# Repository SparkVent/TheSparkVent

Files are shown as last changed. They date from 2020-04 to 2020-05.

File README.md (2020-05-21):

# The Campbell Spark Vent

The Campbell Spark Vent is an open-source Venturi-based ventilator design for emergency use during the COVID-19 pandemic.

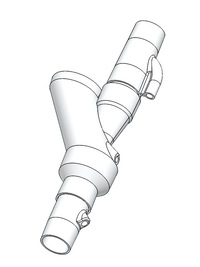
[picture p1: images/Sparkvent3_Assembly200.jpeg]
Sparkvent3 Assembly

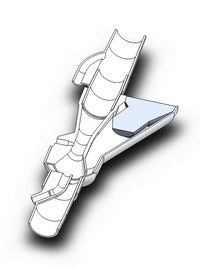
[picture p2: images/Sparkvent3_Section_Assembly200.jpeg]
Sparkvent3 Section_Assembly

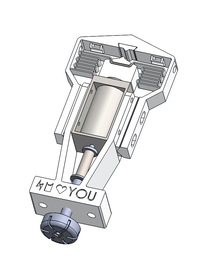
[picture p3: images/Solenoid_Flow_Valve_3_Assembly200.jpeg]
Solenoid Flow Valve 3 Assembly

Campbell SparkVent3 Venturi

Our aim is to make the simplest, safest ventilator we can for the lowest cost and the easiest to manufacture.

[Dr Duncan Campbell](http://www.anzca.edu.au/about-anzca/history-and-heritage/anaesthesia-stories/dr-duncan-campbell), the inventor of the [Campbell Ventilator](https://journals.sagepub.com/doi/pdf/10.1177/0310057X1204000601), created the initial Venturi circuit design as a means to provide a simple and safe ventilator design for the COVID-19 pandemic. The Venturi eliminates the need for bellows and hence, radically simplifies the design, construction and operation of the ventilator.

Our team has refined his original design to it's current version.

We provide this design to anyone who wishes to use it, make it or improve it to help save lives during the COVID-19 pandemic.

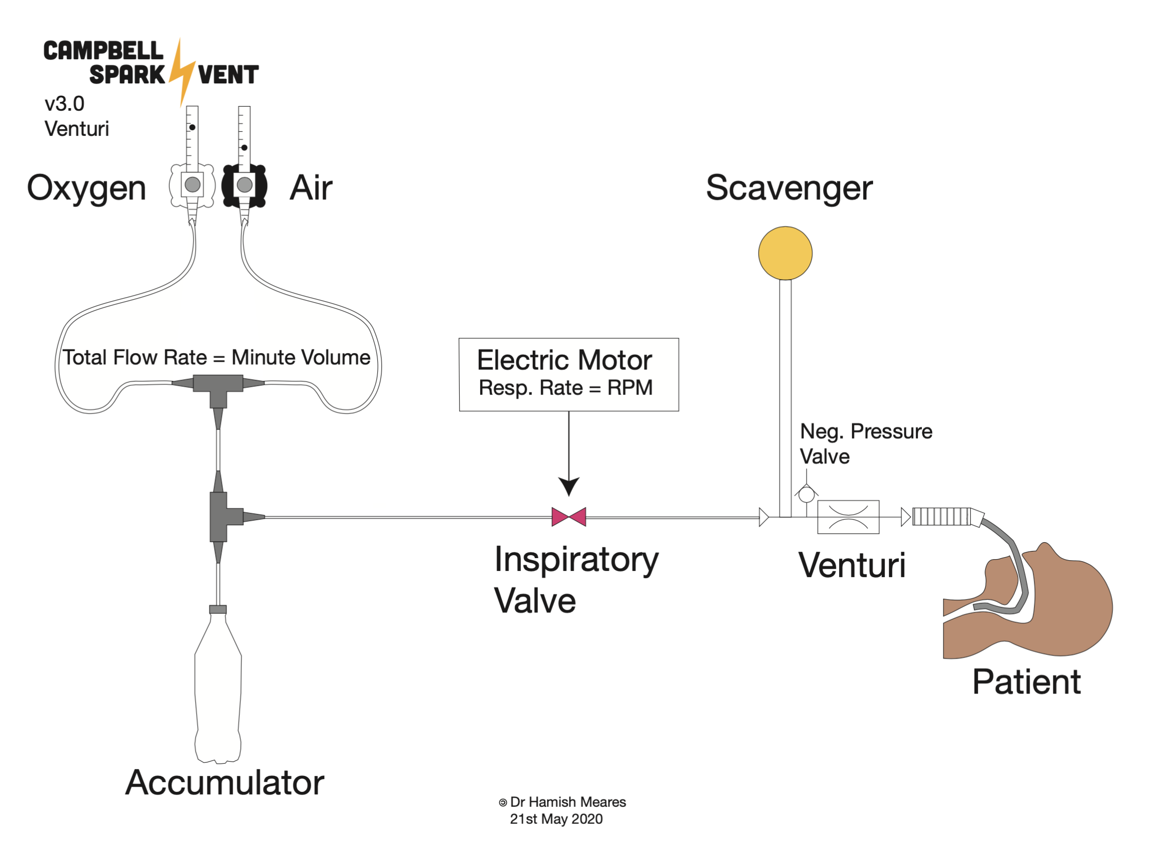
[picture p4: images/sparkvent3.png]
Overview

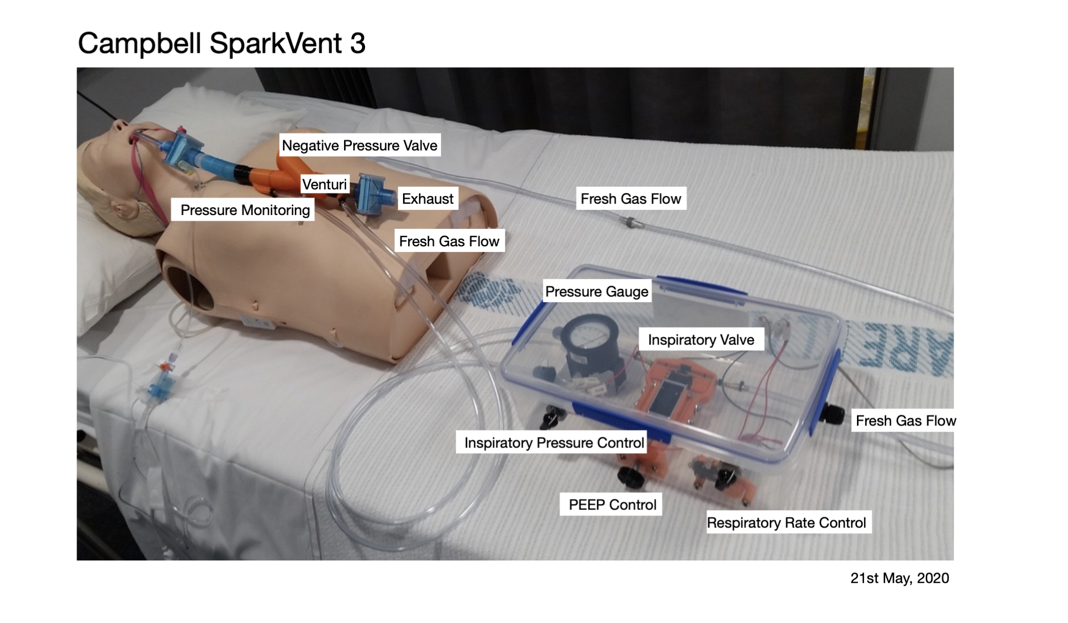
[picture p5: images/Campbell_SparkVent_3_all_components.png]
Campbell SparkVent3 all components

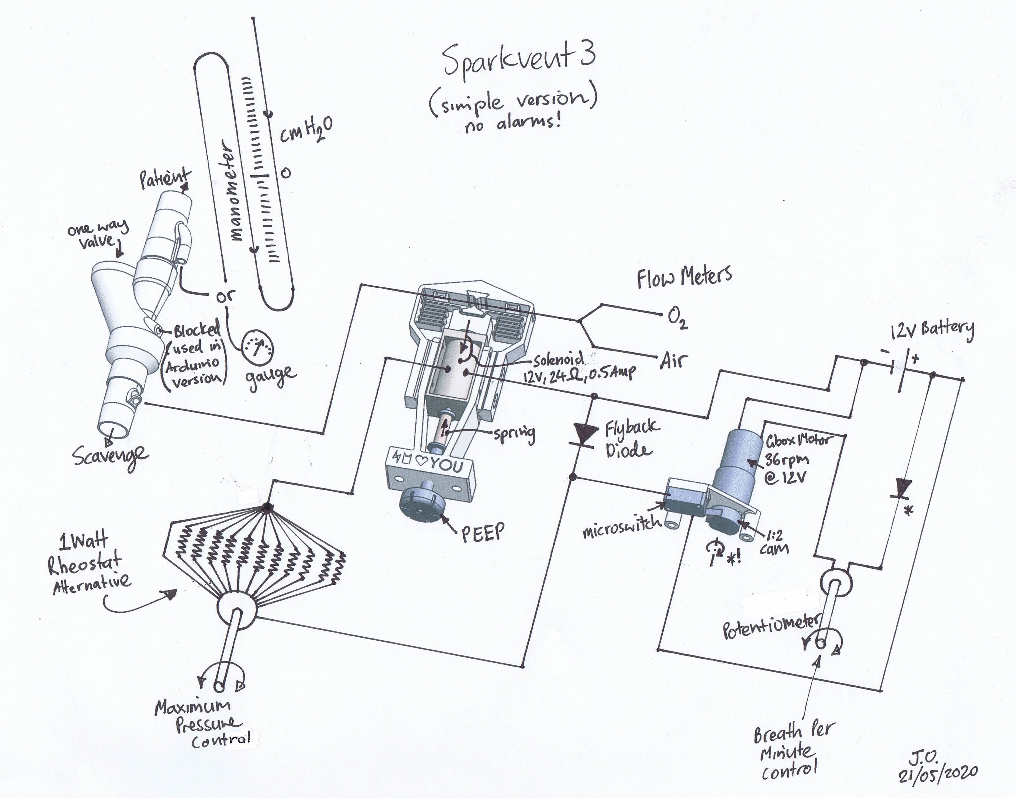
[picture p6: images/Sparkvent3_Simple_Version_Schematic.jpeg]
Sparkvent3 Simple Version Schematic


## Technical Details

The operator sets respiratory rate and also the minute volume and oxygen concentration using two flow meters for oxygen and air. The energy to drive the ventilator comes from the potential energy stored in the pressured gas. The only moving part in the ventilator is the inspiratory valve that operates via a solenoid that compresses a silicon tube that carries the fresh gas flow. The energy consumption of the solenoid valve is very low at around 6W and could be run from a battery if needed. The inspiratory and PEEP pressures are delivered via the venturi. Inspiratory pressure can be set by increasing the fresh gas flow rate, PEEP is set mechanically by turning a screw that sets the minimum pressure in the system. Pressure is monitored using a simple water manometer. The venturi mechanism provides a physical fail-safe as if the pressure in the fresh gas flow is increased to 400kPa (typical hospital gas pressure), the pressure delivered by the venturi is only around 5kPa, (50cmH2O) and the rest of the pressure is dissipated to the exhaust, as the narrow throat of the venturi naturally limits the pressure delivered.

The venturi must sit very close to the endotracheal tube to minimise dead space. The minimal dead space is necessary to minimise the time it takes for the system to reach it's target inspiratory pressure as ideally we would like a square wave pressure waveform.

This design is deliberately 'bare bones'. Ideally it should be used in conjunction with an oxygen saturation probe and an end-tidal carbon dioxide monitor to ensure the patient is adequately ventilated. We are in the process of adding a pressure and flow sensors so we can add alarm systems to this design.

### Aims

* **Works** - as close to these [TGA (Australian Regulatory Body) Guidelines](https://www.tga.gov.au/sites/default/files/ventilator-covid-19-use-australia.pdf) or the more extensive [UK Rapidly Manufactured Ventilator System Specifications](https://assets.publishing.service.gov.uk/government/uploads/system/uploads/attachment_data/file/876167/RMVS001_v3.1.pdf) as we can get it
* **Simple** - as we can get it
* **Safe** - as we can get it
* **Reliable** - as we can get it = ideally do 250,000 cycles without failure
* **Easy to make** - as we can get it
* **Made from existing medical equipment and easily-sourced industrial equipment** - where possible

### Immediate Goal
Provide a ventilator of last-resort for hospitals that have been overwhelmed by the sheer number of COVID-19 patients that require life-saving ventilation.

### Long term Goal
Develop a ventilator that could be used in developing countries to help save lives.

### Testing
We have performed bench testing of the pressure, flow and volume characteristics  on a test-lung in a hospital biomedical workshop (Graphs below). We are currently performing reliability testing of the solenoid 3D-printed valve. Next phase we will be adding alarms and usability testing.
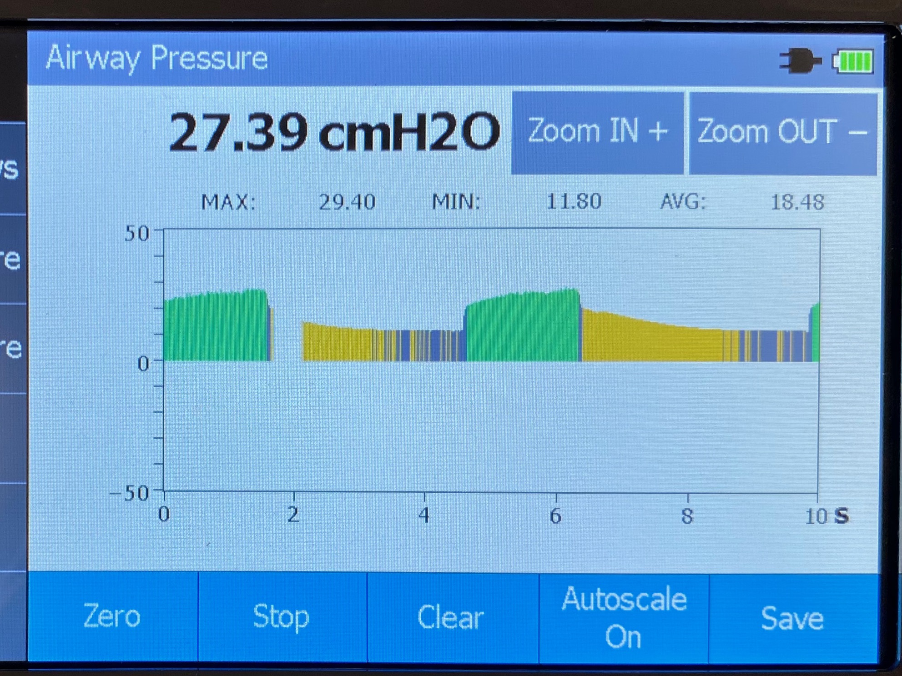
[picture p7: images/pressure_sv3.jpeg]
pressure graph

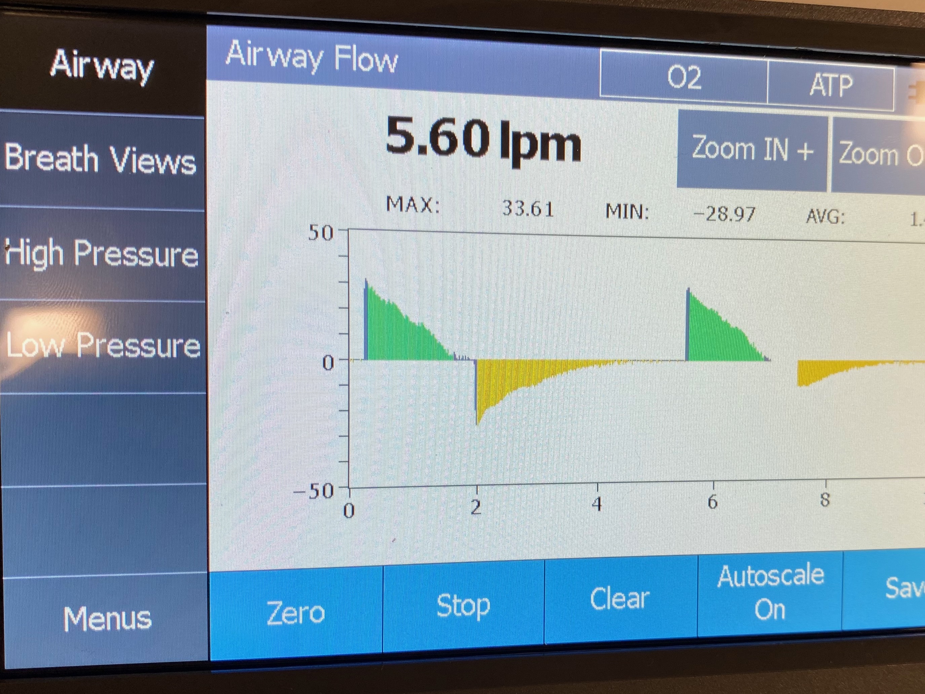
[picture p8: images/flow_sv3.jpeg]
flow graph

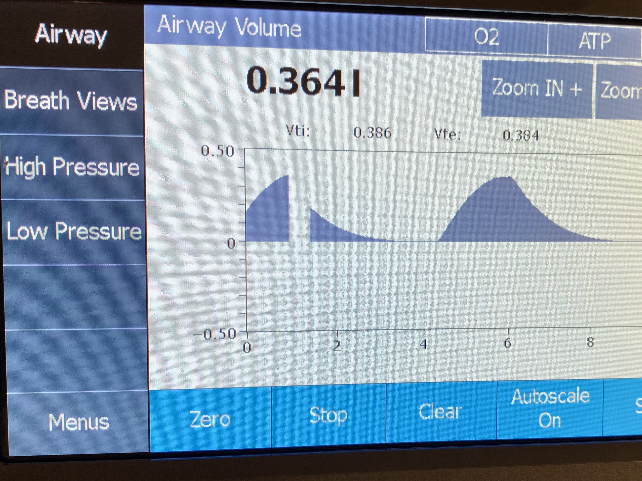
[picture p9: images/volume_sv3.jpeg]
volume graph


## Team

* Dr Hamish Meares, Anaesthetic Doctor/Engineer
* Dr Duncan Campbell, Anaesthetic Doctor (retired) /Inventor of the Campbell Ventilator
* Benjamin Brice, Industrial Designer
* Graham Brice, Biomedical Engineer
* Pete Micallef, CNC Tech & Design, Regal Machinery Services
* Jamie Oorschot, Mechanical Engineer
* Jeremy Funke, Electrical Engineer
* Ray Aunei Mose, Biomedical Engineer
* Peter Humble, IT / Web designer
* With some much appreciated mechanical design help from the University of Newcastle’s Discipline of Mechanical Engineering

## Much Appreciated Support

* [Hall & Wilcox Lawyers](https://hallandwilcox.com.au)
* Dr Carl Hughes, Anaesthetic Doctor & GP
* Dr David Campbell, Anaesthetic Doctor
* Dr Keith Streatfield, Anaesthetic Doctor
* Dr Steve Pickering, Anaesthetic Doctor

## Disclaimer
THE SPARK VENT HAS NOT BEEN TESTED FOR SAFETY AND ITS SAFETY AND PERFORMANCE HAS NOT BEEN EVALUATED OR CONFIRMED. IT SHOULD ONLY BE CONSIDERED FOR USE AS AN ABSOLUTE LAST-RESORT OPTION IN A LIFE-THREATENING EMERGENCY SITUATION. THIS VIDEO IS PROVIDED FOR EDUCATIONAL AND INFORMATIVE PURPOSES DURING A GLOBAL HEALTH EMERGENCY FOR THE CORONA VIRUS PANDEMIC. WE HAVE SOUGHT TO FOLLOW THE UK AND AUSTRALIAN GUIDELINES (TGA) FOR AN EMERGENCY VENTILATOR DESIGN FOR THE PANDEMIC BUT HAVE DEVIATED SIGNIFICANTLY WITH OUR CHOICE IN MATERIALS AND THE ABSENCE OF ANY ALARMS.

IN NO EVENT SHALL THE SPARKVENT TEAM, BE LIABLE TO ANY PARTY FOR DIRECT, INDIRECT, SPECIAL, INCIDENTAL, OR CONSEQUENTIAL DAMAGES, INCLUDING LOST PROFITS, ARISING OUT OF THE USE OF THESE SPECIFICATIONS, LIST OF MATERIALS, ELECTRONIC DESIGNS , SOFTWARE CODE AND ANY DOCUMENTATION, EVEN IF THE SPARKVENT TEAM HAS BEEN ADVISED OF THE POSSIBILITY OF SUCH DAMAGE. THE SPARKVENT TEAM DISCLAIMS ANY WARRANTIES, INCLUDING, BUT NOT LIMITED TO, THE IMPLIED WARRANTIES OF MERCHANTABILITY AND FITNESS FOR A PARTICULAR PURPOSE. THE SOFTWARE AND ACCOMPANYING DOCUMENTATION, SPECIFICATIONS, LIST OF MATERIALS, ELECTRONIC DESIGNS, SOFTWARE CODE AND ANY DOCUMENTATION IF PROVIDED HEREUNDER IS PROVIDED "AS IS". THE SPARKVENT HAS NO CLAIM THAT IT IS COMPLETED OR FUNCTIONAL AND HAS NO OBLIGATION TO PROVIDE MAINTENANCE, SUPPORT, UPDATES, ENHANCEMENTS, OR MODIFICATIONS. RISKS INCLUDE BUT ARE NOT LIMITED TO SERIOUS PHYSICAL INJURY, BURNS, DISABILITY AND/OR DEATH TO BOTH THE PATIENT AND THE OPERATOR.

## Copyright

<br /><span xmlns:dct="http://purl.org/dc/terms/" property="dct:title">SparkVent</span> by <a xmlns:cc="http://creativecommons.org/ns#" href="Sparkvent.org" property="cc:attributionName" rel="cc:attributionURL">SparkVent</a> is licensed under a <a rel="license" href="http://creativecommons.org/licenses/by-nc-sa/4.0/">Creative Commons Attribution-NonCommercial-ShareAlike 4.0 International License</a>.<br />Based on a work at <a xmlns:dct="http://purl.org/dc/terms/" href="Sparkvent.org" rel="dct:source">Sparkvent.org</a>.<br />Permissions beyond the scope of this license may be available at <a xmlns:cc="http://creativecommons.org/ns#" href="Sparkvent.org" rel="cc:morePermissions">Sparkvent.org</a>.

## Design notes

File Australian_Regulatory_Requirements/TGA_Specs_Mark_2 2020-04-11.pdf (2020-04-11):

Spark Vent Mark II

Mark II Mark II | Yes/No/Unknown/ InProgress/NA

## Required Features

### Mandatory ventilation

•the operator can set a tidal volume and respiratory rate. The output will be selected by the operator to be either pressure-controlled ventilation (PCV) or volume-controlled ventilation (VCV) | Yes

### Positive end expiratory pressure (PEEP)

•range from 5 to 25 cm H2O adjustable in increments of 2 cm H2O or smaller | Yes
•patient breathing system must remain pressurised to at least the PEEP level setting at all times | Yes

### Respiratory rate

•range from 5 to 30 breaths per minute adjustable in increments of 2 or smaller | Yes

### Tidal volume (Vt)

•range from at least 200 mL to 800 mL, adjustable in increments of 50 mL or smaller. | Yes
•inspiratory Jlow rate up to 100 litres per minute | Unknown
•inspiratory time adjustable from 0.5 seconds to 2 seconds | No

### Airway pressure safety

•peak inspiratory pressure should adapt to achieve the set tidal volume and… | No
•have an operator-adjustable limit up to 50 cm H2O | Yes
•a mechanical failsafe valve must open at 80 cm H2O | Yes

### Inspired oxygen proportion (FiO2)

•range up to 100%, adjustable in increments of 5% or smaller | Yes
•the ventilator must present 22 mm outside diameter (OD) ‘male’ standard connectors for connection to operator-supplied 22 mm ‘female’ connectors on the breathing system | Yes
•All elements in the gas pathway must meet biological safety and oxygen safety standards for 100% oxygen, especially to minimise risk of Jire or contamination of the patient’s airway | Unknown

### Oxygen supply to ventilator

•all gas connectors and hoses must use standard non-interchangeable connectors and be colour coded according to AS 2902-2005 or equivalent standards | Yes
•must connect to wall pipeline oxygen supply via Sleeve Index System (SIS) deJined in AS 2896-2011 or equivalent. Assume oxygen pipeline pressure is in the range 400 kPa (4 bar) to 500 kPa | Yes
•must be able to be operated on any attached oxygen cylinder connected via SIS and Jitted with a 400 kPa output regulator | Yes

### Air supply to ventilator

•it is preferable not to require pressurised air, as it will not be available in all care areas in pandemic conditions, however if pressurised air is required for ventilator operation: | Yes
•all gas connectors and hoses must use standard non-interchangeable connectors and be colour coded according to applicable standards | In Progress
•must connect to the wall pipeline air supply via SIS | Yes
•Assume wall pipeline pressure is in the range 400 kPa (4 bar) to 500 kPa | Yes

### Displays

•current settings of tidal volume, frequency, inspiratory time, PEEP, FiO2, ventilation mode:
•tidal volume | Yes
•frequency | Yes
•inspiratory time | No
•PEEP | Yes
•FiO2 | Yes
•ventilation mode | Yes
•mechanical displays on control devices such as knobs and sliders are acceptable | Yes

Mark II | Yes/No/Unknown/ InProgress/NA

### Alarms

Must generate an audible alarm at:
•gas or electricity supply failure | No
•machine switched off while connected to a patient | No
•inspiratory and PEEP pressure not achieved | No
•expiratory tidal volume not achieved by 10% | No
•inspiratory tidal volume exceeded by 10% | No

### Electricity supply

•240V AC mains | Yes
•20 minutes backup battery in case of mains electricity failure | No
•should avoid RF or EM emissions that could interfere with other critical machinery | Unknown

### Miscellaneous

•must achieve 100% operating duty cycle for at least 14 days | Unknown
•must include instructions for use and trouble shooting | In Progress
•clear labelling of all critical functions and controls using standard terms, pictograms and colours that will be readily recognised by Australian healthcare staff | In Progress
•must have transparent design, supply chain, manufacture and testing processes and Jield service arrangements that are of sufJicient quality to enable health department ofJicials and Therapeutic Goods Administration (TGA) ofJicials to deem them appropriate for usage in exceptional circumstances | No
•must be able to be moved easily within hospital premises | Yes
•must be amenable to standard disinfection and cleaning procedures | Yes
•must be made from materials and parts, including disposables, that are readily available in the Australian supply chain (anticipating increasing global restrictions on freight movement): | Yes
1. Materials of Construction (raw materials)
a.The chosen material must be reasonably pure and simple in nature (minimise the use of additives where possible) | Yes
a.For components requiring Jlexibility avoid the use of materials requiring plasticisers. Good candidates are those materials that belong to the polyoleJin family, examples include polyethylene and polypropylene | Yes
a.For structural components, materials such as polycarbonate or acrylonitrile butadiene styrene (ABS) should be used without additives, although reinforcement with glass Jibre would be acceptable | Yes
a.Polyvinyl chloride (PVC) must be avoided in the patient gas pathway | No
a.PVC should be avoided elsewhere | No

2.Manufacturing Process (risk from contaminants)
a.Mould release agents used within extrusion or injection moulding techniques may be required in setting up the machine, they should not be needed once a process is in full scale production | NA
a.Approximately, the Jirst 20 or so items in an injection moulding production run should be discarded to minimise risk from contamination with mould release agents | NA
a.Extrusion and moulding techniques are comparatively simple and well controlled; therefore, ventilators will not be required to be manufactured within cleanroom speciJications | NA
a.Manufacture in a reasonably clean room and protection of components and products from contamination should sufJice | Yes

a.If a-d above are followed, chemical or particulate testing of the air coming out of the breathing circuit should not be necessary

3. Hazard Mitigation
a.Particulate matter: solid particles suspended in a gas. Particulate matter emissions are not of signiJicant concern if the manufacturing process is adequately controlled as per the above criteria | Unknown
a.Volatile organic compound (VOC): organic compound whose boiling point is in the range of 50⁰C to 260⁰C. Risk of exposure to VOCs can be minimised through the appropriate choice of materials as set out in section 1 (materials of construction) | Yes
a.Leachable substances (in condensate): chemicals removed from the medical device by the action of water, other liquids or other gases related to the use of the medical device. Ensure an HME Jilter is used between the ventilator and breathing system. | Yes

### Other relevant standards

| Yes/No/Unknown/ InProgress/NA

•See Appendix A, Relevant Standards and Documents
•Device veriJication and validation testing must be carried out by the manufacturer. Testing should be aligned to the requirements in the UK MHRA guidelines in Appendix B (Testing protocol for Jinal validation of safety and performance of RVMS) at | In Progress

https://assets.publishing.service.gov.uk/government/uploads/system/uploads/attachment_data/Jile/876167/RMVS001_v3.1.pdf (https://assets.publishing.service.gov.uk/government/uploads/system/uploads/attachment_data/file/876167/RMVS001_v3.1.pdf)

•Rapidly manufactured ventilators are likely to include software. Included software falls under the deJinition of a medical device and must meet requirements that will ensure product performance and safety. See Appendix C (software development requirements) from the MHRA guideline at the link above. | No

## Desirable Features

### Spontaneous ventilation

•the operator sets an inspiratory pressure and PEEP. The ventilator will sense when a patient starts to breathe in and apply the operator-speciJied inspiratory pressure, then sense when the patient starts to breathe out and apply the operator-speciJied expiratory pressure. | No
•If the patient stops breathing in pressure support mode, it must failsafe automatically to mandatory ventilation. | Yes

### Synchronized mandatory ventilation

•same as mandatory ventilation but mandatory breaths are synchronized to patient effort through Jlow sensing or pressure sensing, also known as synchronized intermittent mandatory ventilation volume control (SIMV-VC) or pressure control (SIMV-PC) | No
•additional inspiratory pressure support for those patients breathing to some extent themselves. | No

### Tidal volume

•capacity to set inspiratory rise-time as a fraction of the inspiratory time, through waveform control or ratio control. | No
•inspiratory Jlow rate up to 150 litres per minute | Unknown

### Exhalation filters

•use modular expiratory components that can be removed for disinfection, and that can vent to long life viral Jilters | Yes

### Gas supply

•can operate using an oxygen concentrator device for input oxygen | Unknown

### Extended battery use

•hot swappable batteries to run on battery supply for an extended period, for example, 2 hours for within-hospital transfer | In Progress

### Alarms

•inspiratory airway pressure exceeded | No
•respiratory rate exceeds a set limit | No

### Displays

•actual achieved measurements of tidal volume, breathing rate, PEEP, peak and plateau pressure, FiO2, inspiratory to expiratory time ratio (I:E) | No
•displayed waveforms of key parameters including but not limited to Jlow, pressure and volume versus time | No
•if it exists, in pressure support mode there must be real-time conJirmation of each patient breath and an alarm if below acceptable range | No

Notes

PCV you set pressures not volumes, you can measure the volumes delivered though

Ventilator has a fixed I:E ratio of one to two, and hence Inspiratory time will be dependent on respiratory rate

Pressure control ventilation mode only, not pressure-volume-guaranteed. Needs operator to adjust pressure to achieve target volume

Pop off at 40cm H20

Does not use 4 bar gas supply directly, instead it uses Australian standard flow meters attached to the 4 bar supply

Uses Standard Sleeve Index as ventilator uses standard flow meters that already meet the Australian Standards.

Requires pressured gas supply, but is very frugal in it’s use, only the patient’s minute volume so around 5-10 L/ min

Uses Standard Sleeve Index as ventilator uses standard flow meters that already meet the Australian Standards.

Fixed I:E ratio 1:2, so inspiratory time will be dependent on respiratory rate

Only does PCV

## Required Features

### Mandatory ventilation

•the operator can set a tidal volume and respiratory rate. The output will be selected by the operator to be either pressure-controlled ventilation (PCV) or volume-controlled ventilation (VCV)

### Positive end expiratory pressure (PEEP)

•range from 5 to 25 cm H2O adjustable in increments of 2 cm H2O or smaller
•patient breathing system must remain pressurised to at least the PEEP level setting at all times

### Respiratory rate

•range from 5 to 30 breaths per minute adjustable in increments of 2 or smaller

### Tidal volume (Vt)

•range from at least 200 mL to 800 mL, adjustable in increments of 50 mL or smaller. •inspiratory Jlow rate up to 100 litres per minute
•inspiratory time adjustable from 0.5 seconds to 2 seconds

### Airway pressure safety

•peak inspiratory pressure should adapt to achieve the set tidal volume and…

•have an operator-adjustable limit up to 50 cm H2O
•a mechanical failsafe valve must open at 80 cm H2O

### Inspired oxygen proportion (FiO2)

•range up to 100%, adjustable in increments of 5% or smaller
•the ventilator must present 22 mm outside diameter (OD) ‘male’ standard connectors for connection to operator-supplied 22 mm ‘female’ connectors on the breathing system
•All elements in the gas pathway must meet biological safety and oxygen safety standards for 100% oxygen, especially to minimise risk of Jire or contamination of the patient’s airway

### Oxygen supply to ventilator

•all gas connectors and hoses must use standard non-interchangeable connectors and be colour coded according to AS 2902-2005 or equivalent standards
•must connect to wall pipeline oxygen supply via Sleeve Index System (SIS) deJined in AS 2896-2011 or equivalent. Assume oxygen pipeline pressure is in the range 400 kPa (4 bar) to 500 kPa
•must be able to be operated on any attached oxygen cylinder connected via SIS and Jitted with a 400 kPa output regulator

### Air supply to ventilator

•it is preferable not to require pressurised air, as it will not be available in all care areas in pandemic conditions, however if pressurised air is required for ventilator operation:
•all gas connectors and hoses must use standard non-interchangeable connectors and be colour coded according to applicable standards
•must connect to the wall pipeline air supply via SIS
•Assume wall pipeline pressure is in the range 400 kPa (4 bar) to 500 kPa

### Displays

•current settings of tidal volume, frequency, inspiratory time, PEEP, FiO2, ventilation mode: •tidal volume
•frequency
•inspiratory time
•PEEP
•FiO2
•ventilation mode
•mechanical displays on control devices such as knobs and sliders are acceptable

Mark II

PVC will be replaced for Mark III

PVC will be replaced for Mark III

Notes

### Alarms

Must generate an audible alarm at:
•gas or electricity supply failure
•machine switched off while connected to a patient •inspiratory and PEEP pressure not achieved •expiratory tidal volume not achieved by 10% •inspiratory tidal volume exceeded by 10%

### Electricity supply

•240V AC mains
•20 minutes backup battery in case of mains electricity failure
•should avoid RF or EM emissions that could interfere with other critical machinery

### Miscellaneous

•must achieve 100% operating duty cycle for at least 14 days
•must include instructions for use and trouble shooting
•clear labelling of all critical functions and controls using standard terms, pictograms and colours that will be readily recognised by Australian healthcare staff
•must have transparent design, supply chain, manufacture and testing processes and Jield service arrangements that are of sufJicient quality to enable health department ofJicials and Therapeutic Goods Administration (TGA) ofJicials to deem them appropriate for usage in exceptional circumstances
•must be able to be moved easily within hospital premises
•must be amenable to standard disinfection and cleaning procedures
•must be made from materials and parts, including disposables, that are readily available in the Australian supply chain (anticipating increasing global restrictions on freight movement):

### 1. Materials of Construction (raw materials)

a.The chosen material must be reasonably pure and simple in nature (minimise the use of additives where possible)
a.For components requiring Jlexibility avoid the use of materials requiring plasticisers. Good candidates are those materials that belong to the polyoleJin family, examples include polyethylene and polypropylene a.For structural components, materials such as polycarbonate or acrylonitrile butadiene styrene (ABS) should be used without additives, although reinforcement with glass Jibre would be acceptable a.Polyvinyl chloride (PVC) must be avoided in the patient gas pathway
a.PVC should be avoided elsewhere

2.Manufacturing Process (risk from contaminants)
a.Mould release agents used within extrusion or injection moulding techniques may be required in setting up the machine, they should not be needed once a process is in full scale production
a.Approximately, the Jirst 20 or so items in an injection moulding production run should be discarded to minimise risk from contamination with mould release agents
a.Extrusion and moulding techniques are comparatively simple and well controlled; therefore, ventilators will not be required to be manufactured within cleanroom speciJications
a.Manufacture in a reasonably clean room and protection of components and products from contamination should sufJice
a.If a-d above are followed, chemical or particulate testing of the air coming out of the breathing circuit should not be necessary

### 3. Hazard Mitigation

a.Particulate matter: solid particles suspended in a gas. Particulate matter emissions are not of signiJicant concern if the manufacturing process is adequately controlled as per the above criteria
a.Volatile organic compound (VOC): organic compound whose boiling point is in the range of 50⁰C to 260⁰C. Risk of exposure to VOCs can be minimised through the appropriate choice of materials as set out in section 1 (materials of construction)
a.Leachable substances (in condensate): chemicals removed from the medical device by the action of water, other liquids or other gases related to the use of the medical device. Ensure an HME Jilter is used between the ventilator and breathing system.

### Other relevant standards

Depends on flow rate of concentrator

Notes

•See Appendix A, Relevant Standards and Documents
•Device veriJication and validation testing must be carried out by the manufacturer. Testing should be aligned to the requirements in the UK MHRA guidelines in Appendix B (Testing protocol for Jinal validation of safety and performance of RVMS) at https://assets.publishing.service.gov.uk/government/uploads/system/uploads/attachment_data/Jile/876167/RMVS001_v3.1.pdf
•Rapidly manufactured ventilators are likely to include software. Included software falls under the deJinition of a medical device and must meet requirements that will ensure product performance and safety. See Appendix C (software development requirements) from the MHRA guideline at the link above.

## Desirable Features

### Spontaneous ventilation

•the operator sets an inspiratory pressure and PEEP. The ventilator will sense when a patient starts to breathe in and apply the operator-speciJied inspiratory pressure, then sense when the patient starts to breathe out and apply the operator-speciJied expiratory pressure.
•If the patient stops breathing in pressure support mode, it must failsafe automatically to mandatory ventilation.

### Synchronized mandatory ventilation

•same as mandatory ventilation but mandatory breaths are synchronized to patient effort through Jlow sensing or pressure sensing, also known as synchronized intermittent mandatory ventilation volume control (SIMV-VC) or pressure control (SIMV-PC)
•additional inspiratory pressure support for those patients breathing to some extent themselves.

### Tidal volume

•capacity to set inspiratory rise-time as a fraction of the inspiratory time, through waveform control or ratio control.
•inspiratory Jlow rate up to 150 litres per minute

### Exhalation filters

•use modular expiratory components that can be removed for disinfection, and that can vent to long life viral Jilters

### Gas supply

•can operate using an oxygen concentrator device for input oxygen

### Extended battery use

•hot swappable batteries to run on battery supply for an extended period, for example, 2 hours for within-hospital transfer

### Alarms

•inspiratory airway pressure exceeded
•respiratory rate exceeds a set limit

### Displays

•actual achieved measurements of tidal volume, breathing rate, PEEP, peak and plateau pressure, FiO2, inspiratory to expiratory time ratio (I:E)
•displayed waveforms of key parameters including but not limited to Jlow, pressure and volume versus time
•if it exists, in pressure support mode there must be real-time conJirmation of each patient breath and an alarm if below acceptable range

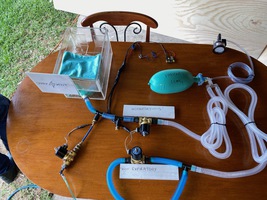
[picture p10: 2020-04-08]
images/basic_overview200.jpeg

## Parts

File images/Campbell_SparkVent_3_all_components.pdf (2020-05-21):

# Campbell SparkVent 3

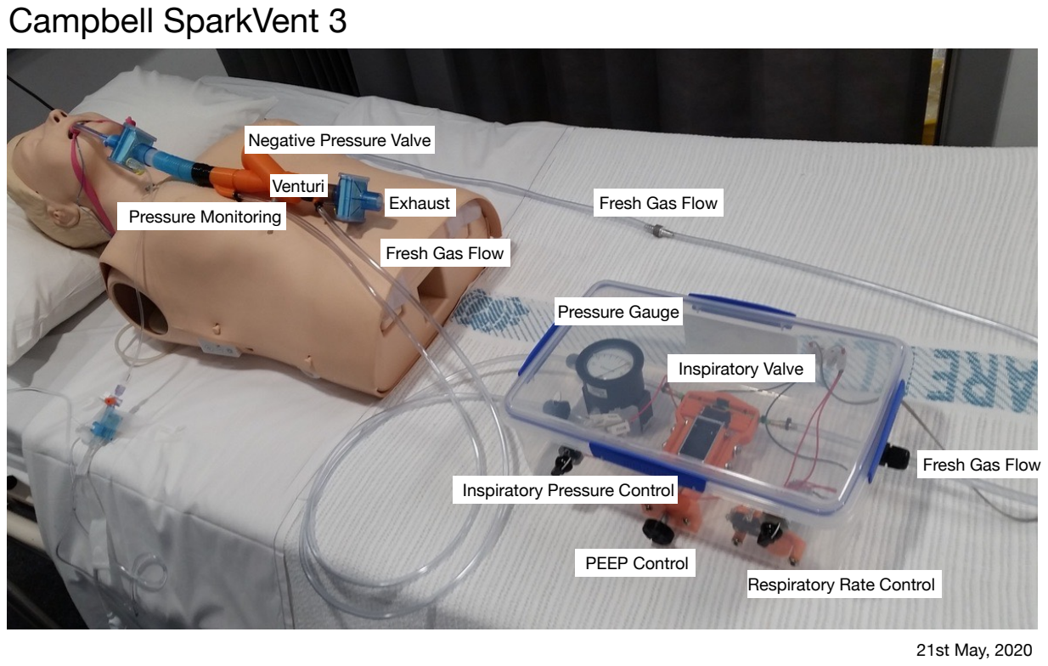
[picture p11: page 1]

Venturi

Negative Pressure Valve

Exhaust
Pressure Monitoring

Inspiratory Valve

Respiratory Rate Control

Fresh Gas Flow

Inspiratory Pressure Control

PEEP Control

Pressure Gauge

Fresh Gas Flow

Fresh Gas Flow

21st May, 2020

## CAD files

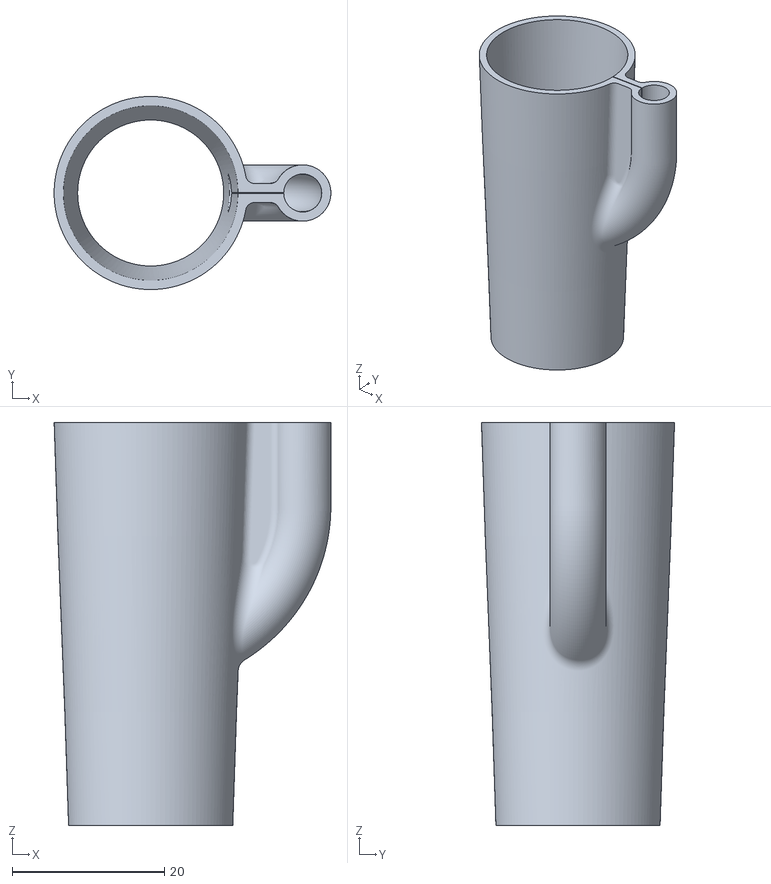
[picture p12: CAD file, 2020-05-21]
3D_Print_Files/Patient Adapter.STL
36.4 x 25.4 x 53.0

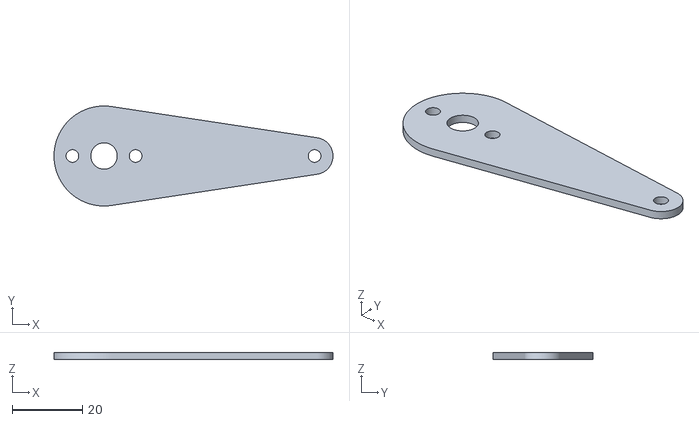
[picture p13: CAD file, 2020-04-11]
3D_Print_Files_for_Cam_Valves/Torque arm.STL
79.5 x 28.5 x 2.00

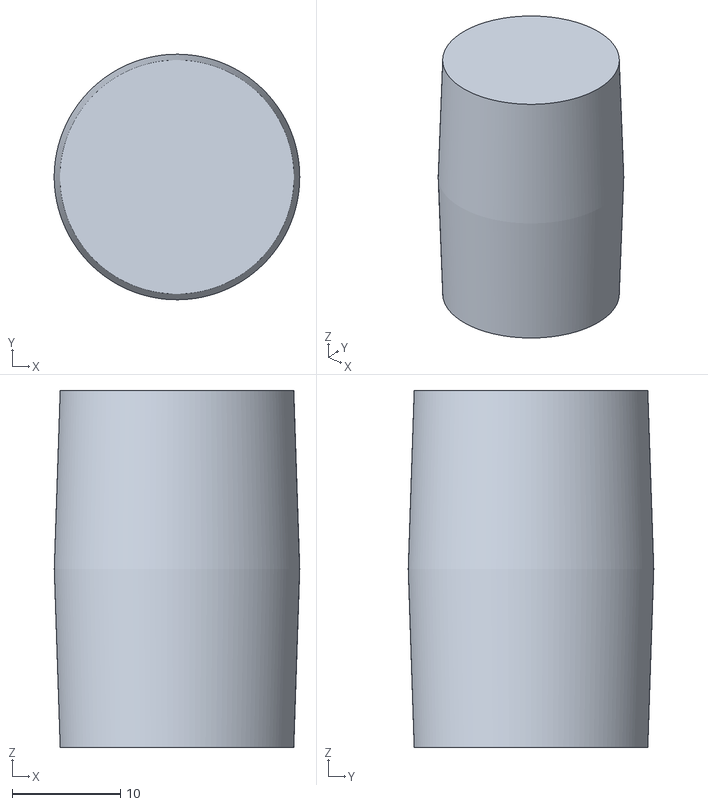
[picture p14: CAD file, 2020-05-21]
3D_Print_Files/Adapter#3 Solid.STL
22.7 x 22.7 x 33.0

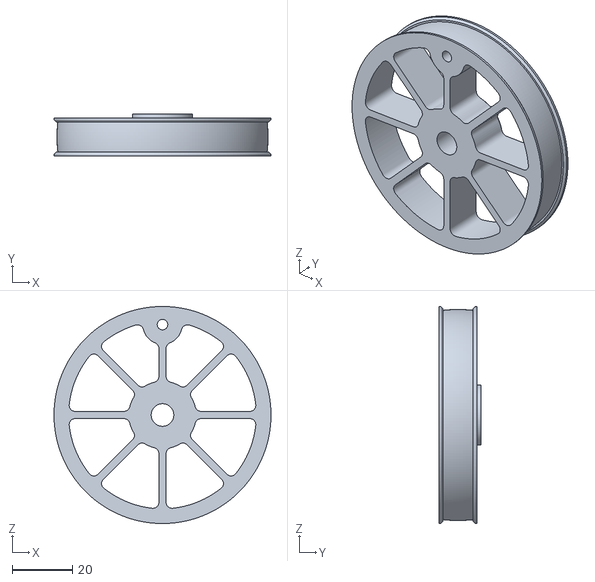
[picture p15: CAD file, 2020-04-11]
3D_Print_Files_for_Cam_Valves/Pulley 10Wx70ODx7.5Bore.STL
72.0 x 14.0 x 72.0

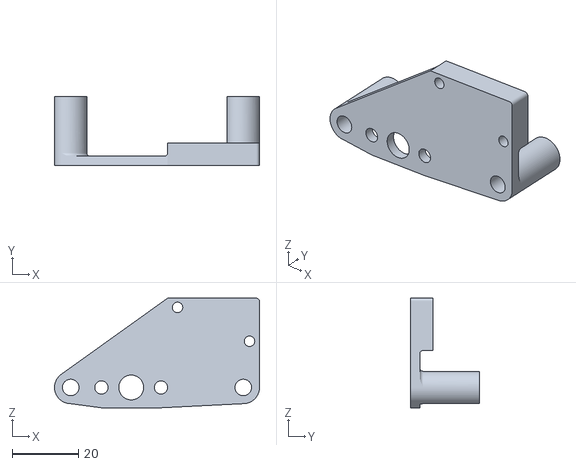
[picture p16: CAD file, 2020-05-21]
3D_Print_Files/Frame.STL
62.0 x 20.8 x 33.2

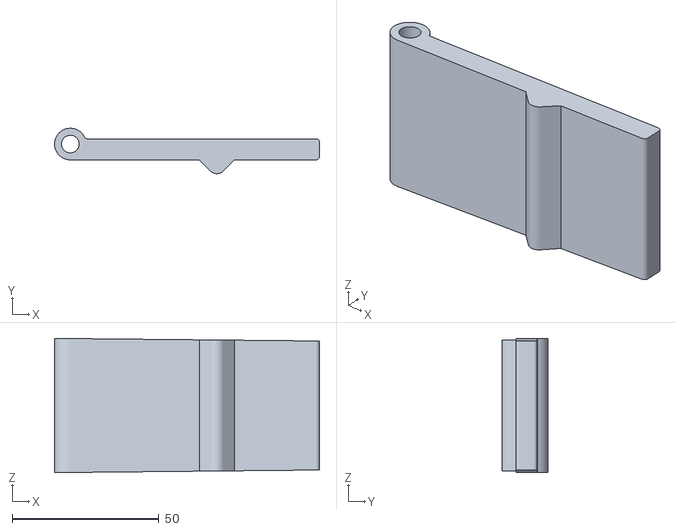
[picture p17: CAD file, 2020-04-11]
3D_Print_Files_for_Cam_Valves/Follower Wide ME.STL
90.4 x 15.5 x 45.8

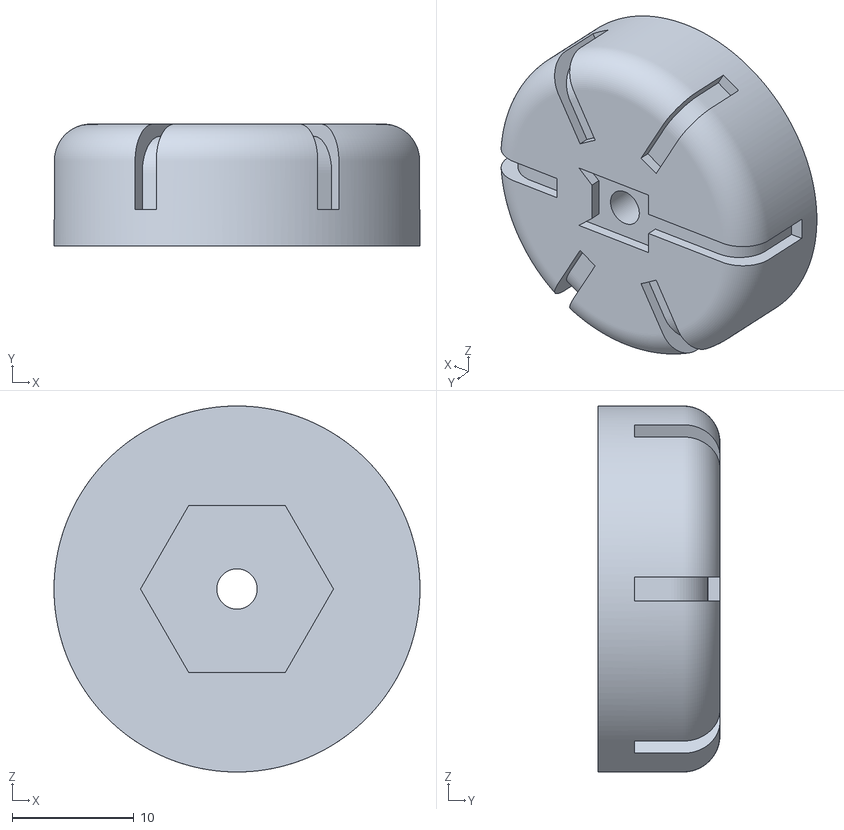
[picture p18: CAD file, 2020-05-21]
3D_Print_Files/Knob.STL
30.0 x 10.0 x 30.0

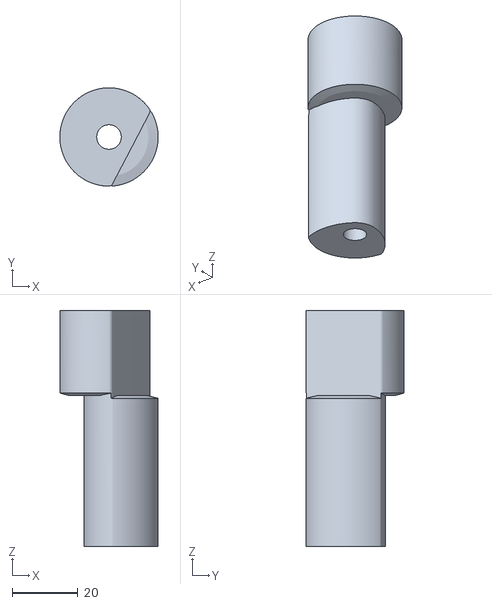
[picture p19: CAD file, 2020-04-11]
3D_Print_Files_for_Cam_Valves/Cam - Bore 7.5.STL
30.0 x 30.0 x 72.0

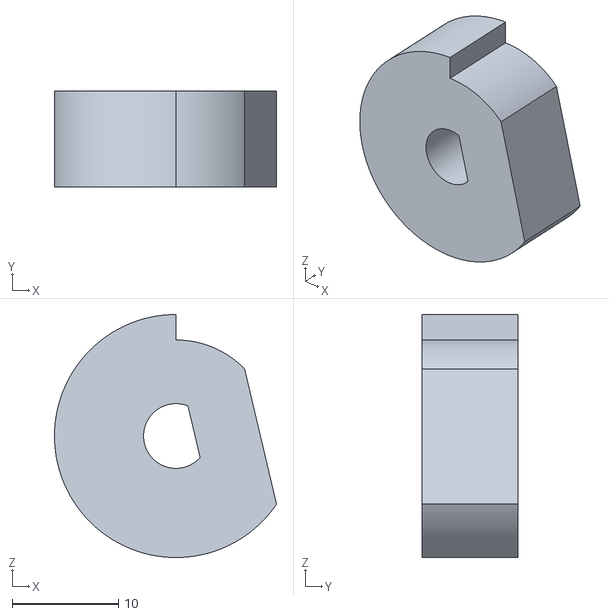
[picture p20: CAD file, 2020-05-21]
3D_Print_Files/Cam Fixed 2to1.STL
20.9 x 9.00 x 22.9

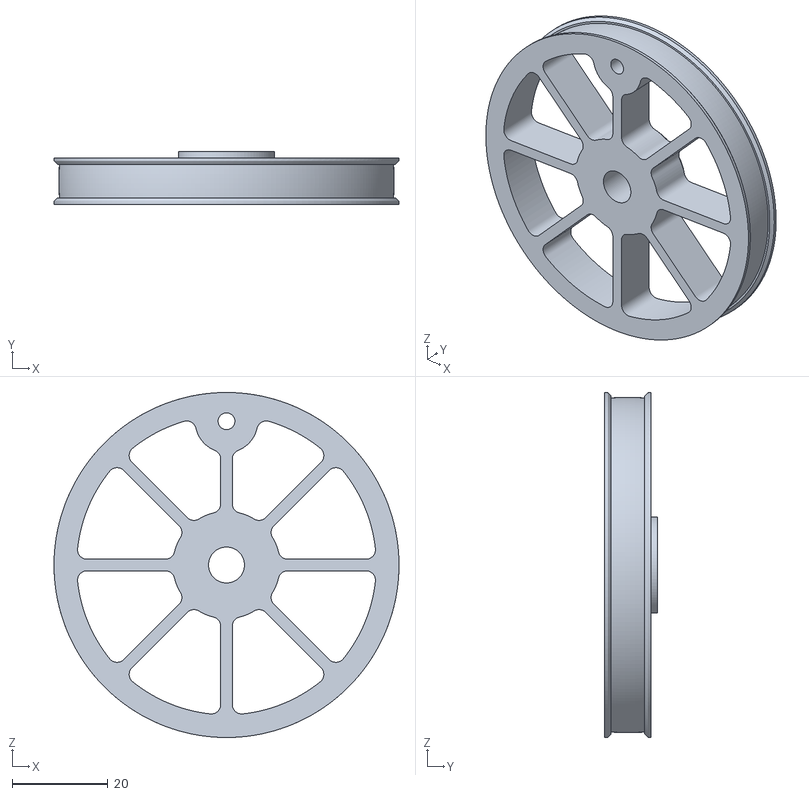
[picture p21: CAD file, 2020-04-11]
3D_Print_Files_for_Cam_Valves/Pulley 7Wx70ODx7.5Bore.STL
72.0 x 11.0 x 72.0

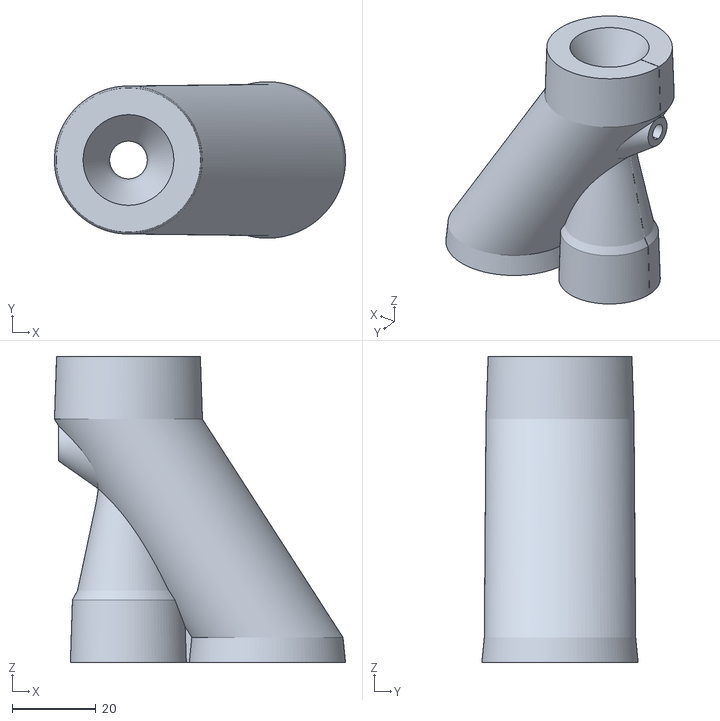
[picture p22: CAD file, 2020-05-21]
3D_Print_Files/Venturi 9mm+port solid.STL
69.6 x 37.4 x 73.2

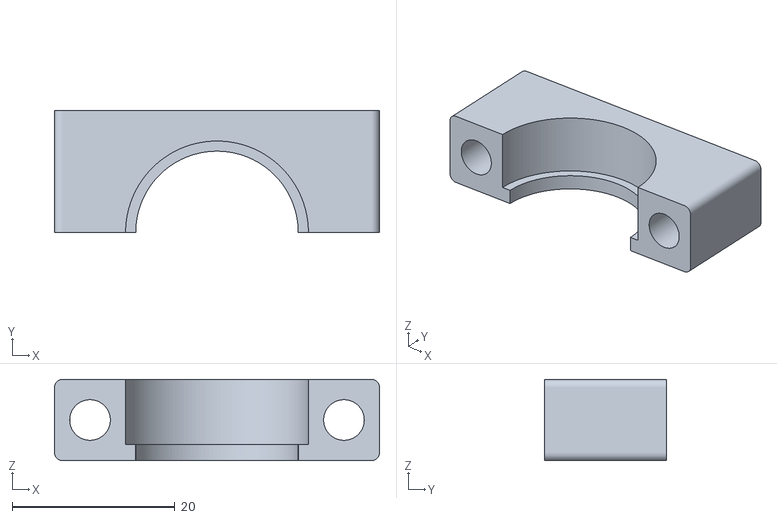
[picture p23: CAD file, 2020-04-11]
3D_Print_Files_for_Cam_Valves/Bearing Cap.STL
40.0 x 15.0 x 10.0

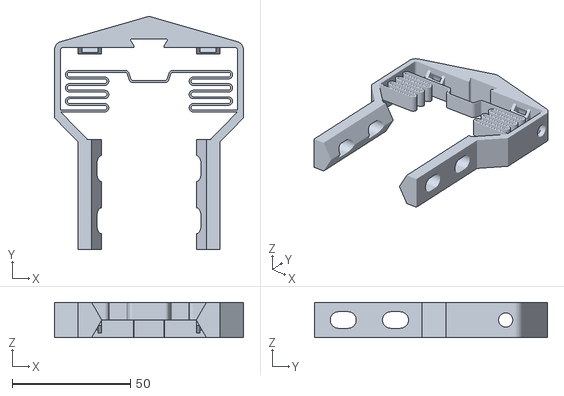
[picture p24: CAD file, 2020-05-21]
3D_Print_Files/Frame & Pinch Spring #5.STL
80.0 x 98.8 x 15.0

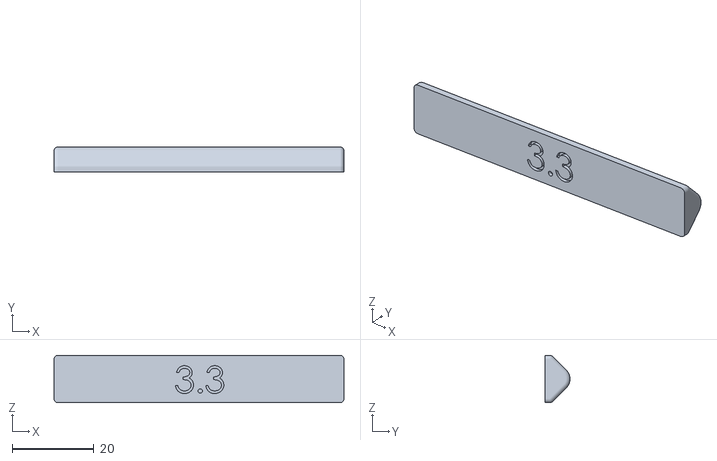
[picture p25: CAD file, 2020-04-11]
3D_Print_Files_for_Cam_Valves/Bottom Pinch 3.3mm Gap.STL
71.0 x 6.15 x 11.6

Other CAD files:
3D_Print_Files/Nozzel Adapter Solid.STL
3D_Print_Files_for_Cam_Valves/Pulley Handle.STL
3D_Print_Files/Top Pinch #5.STL
3D_Print_Files_for_Cam_Valves/Torque arm Linkage.STL
3D_Print_Files/Adapter#1 Solid.STL
3D_Print_Files/Adapter#1.STL
3D_Print_Files/Adapter#3.STL
3D_Print_Files/Bottom Pinch #5.STL
3D_Print_Files/Check Valve #2 Solid.STL
3D_Print_Files/Nozzel Adapter.STL
3D_Print_Files/Patient Adapter Solid.STL
3D_Print_Files/Solenoid Mounting Frame.STL
3D_Print_Files/Venturi 9mm+port.STL
3D_Print_Files_for_Cam_Valves/Base.STL
3D_Print_Files_for_Cam_Valves/Bottom Pinch 3.5mm Gap.STL
3D_Print_Files_for_Cam_Valves/Bottom Pinch 3.7mm Gap.STL
3D_Print_Files_for_Cam_Valves/Cam - Bore 8.0.STL
3D_Print_Files_for_Cam_Valves/Follower Narrow I.STL

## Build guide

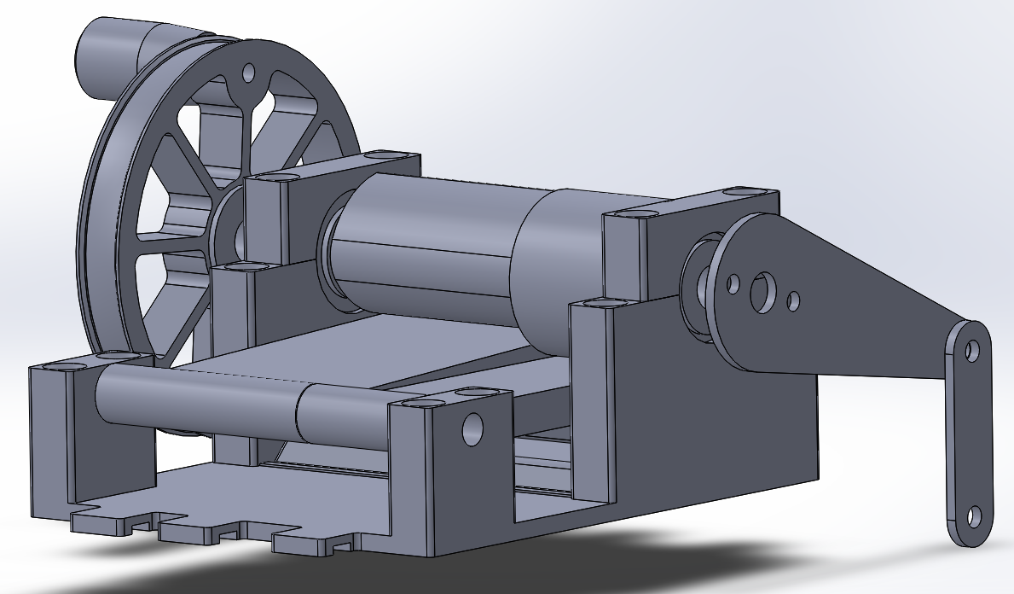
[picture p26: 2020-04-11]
images/Solidworks - Assembly.png

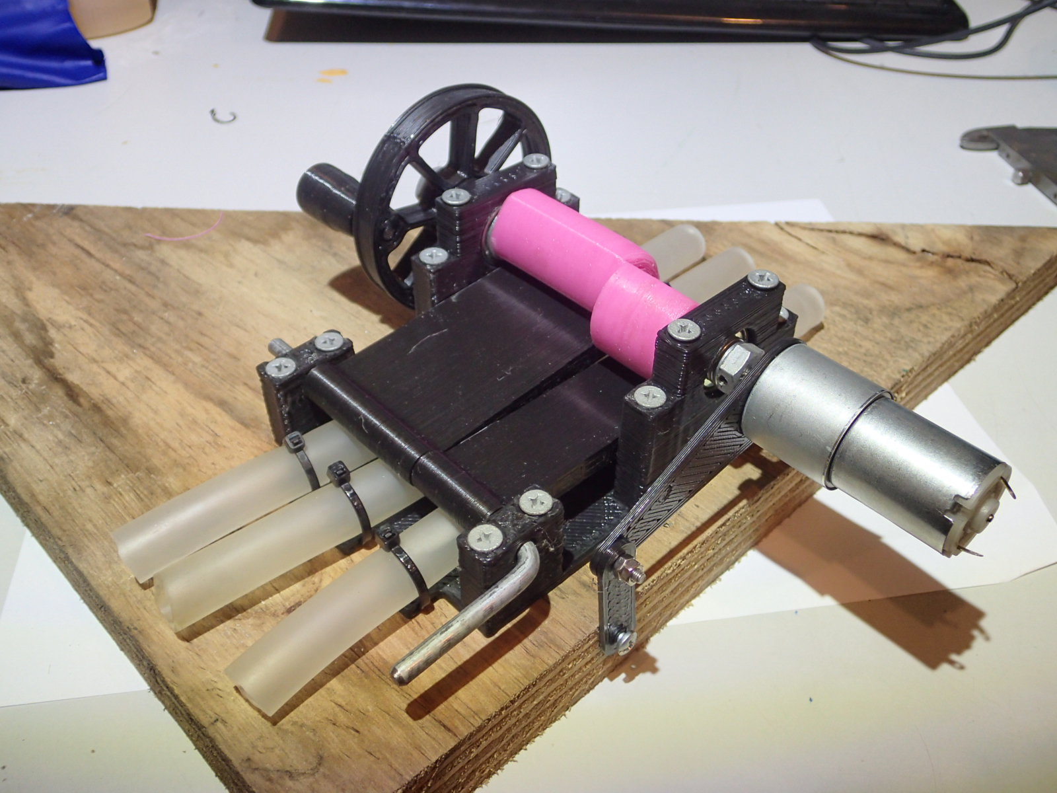
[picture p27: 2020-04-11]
images/Assembly_Photo.JPG

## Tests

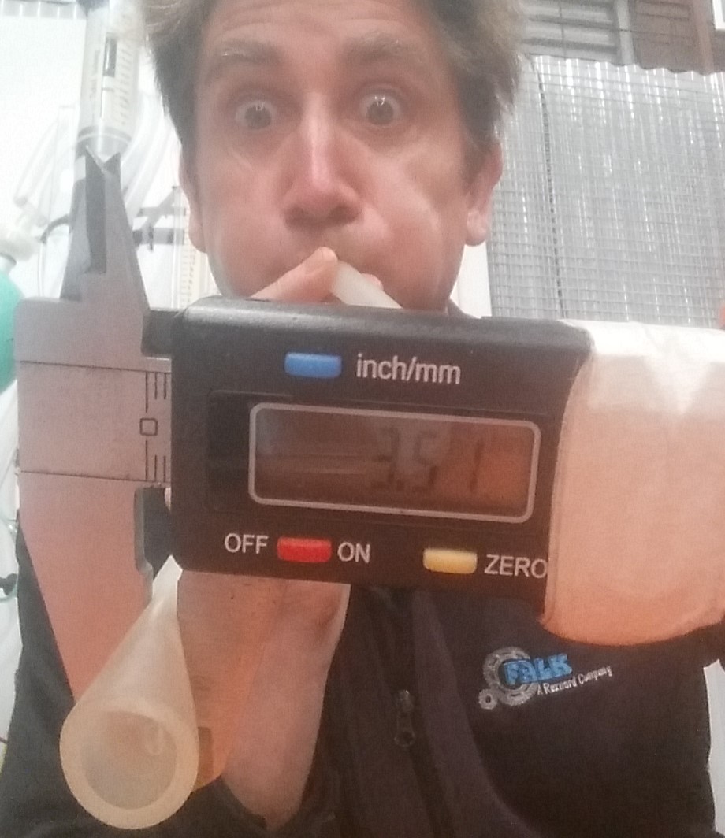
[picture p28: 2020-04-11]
images/Measure_Pinch_Gap.jpg

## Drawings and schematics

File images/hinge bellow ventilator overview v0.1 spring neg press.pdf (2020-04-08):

## Oxygen Air

## Scavenger

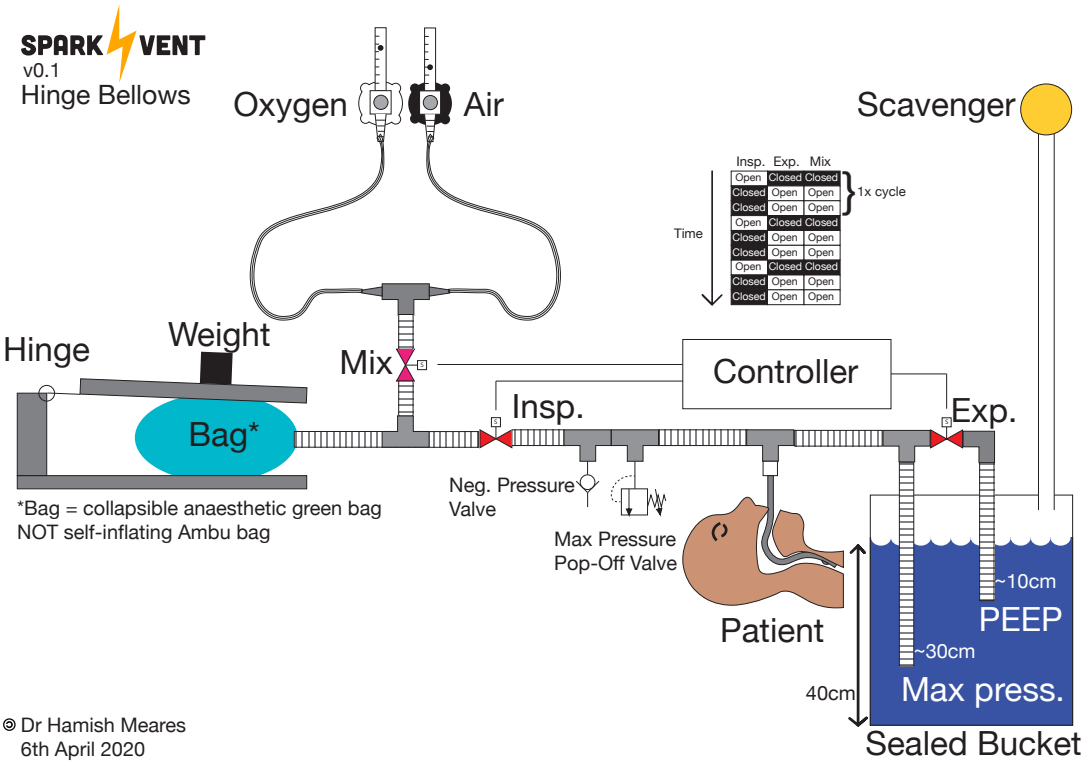
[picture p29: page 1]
Mix; Insp.; Exp.; PEEP Max press.; Bag*; Weight; Patient; Hinge; Controller; Neg. Pressure Valve; 1x cycle }; Hinge Bellows

Insp. Exp. Mix
Open Closed Closed
Closed Open Open
Time

*Bag = collapsible anaesthetic green bag
NOT self-inflating Ambu bag

Max Pressure
Pop-Off Valve

Sealed Bucket Dr Hamish Meares
6th April 2020

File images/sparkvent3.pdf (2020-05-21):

## Oxygen Air

## Scavenger

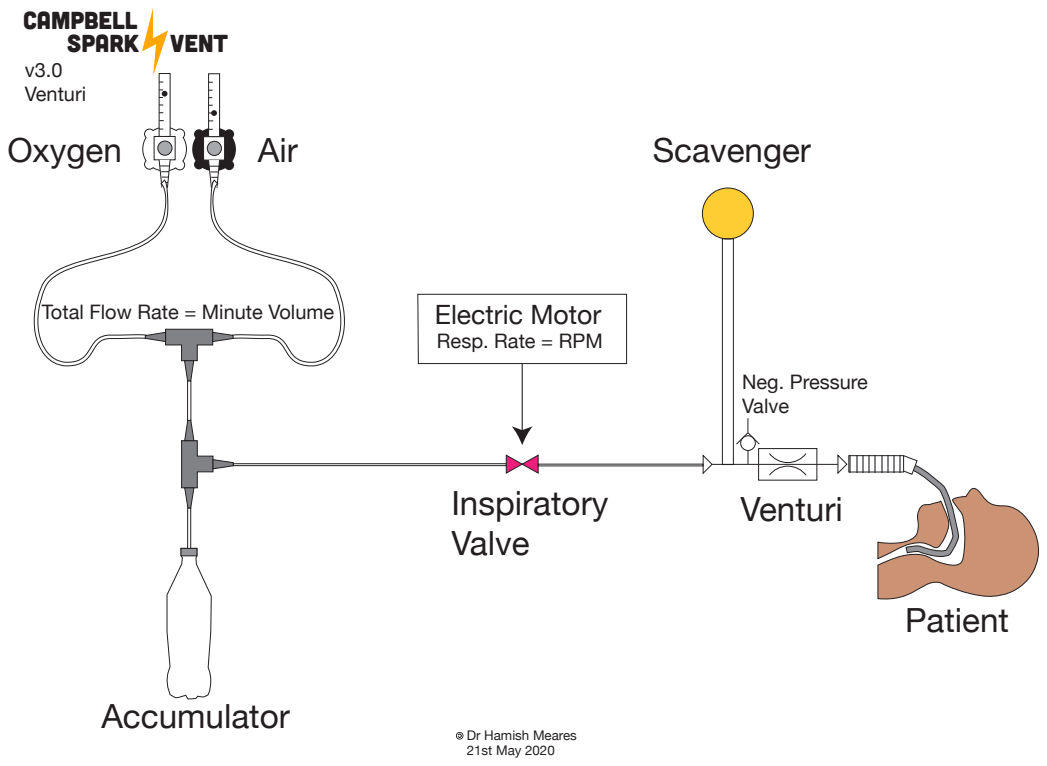
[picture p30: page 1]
Inspiratory Valve; v3.0 Venturi; Accumulator; Patient; Venturi; Neg. Pressure Valve; SPARK VENT; CAMPBELL

Total Flow Rate = Minute Volume

Electric Motor
Resp. Rate = RPM

Dr Hamish Meares
21st May 2020

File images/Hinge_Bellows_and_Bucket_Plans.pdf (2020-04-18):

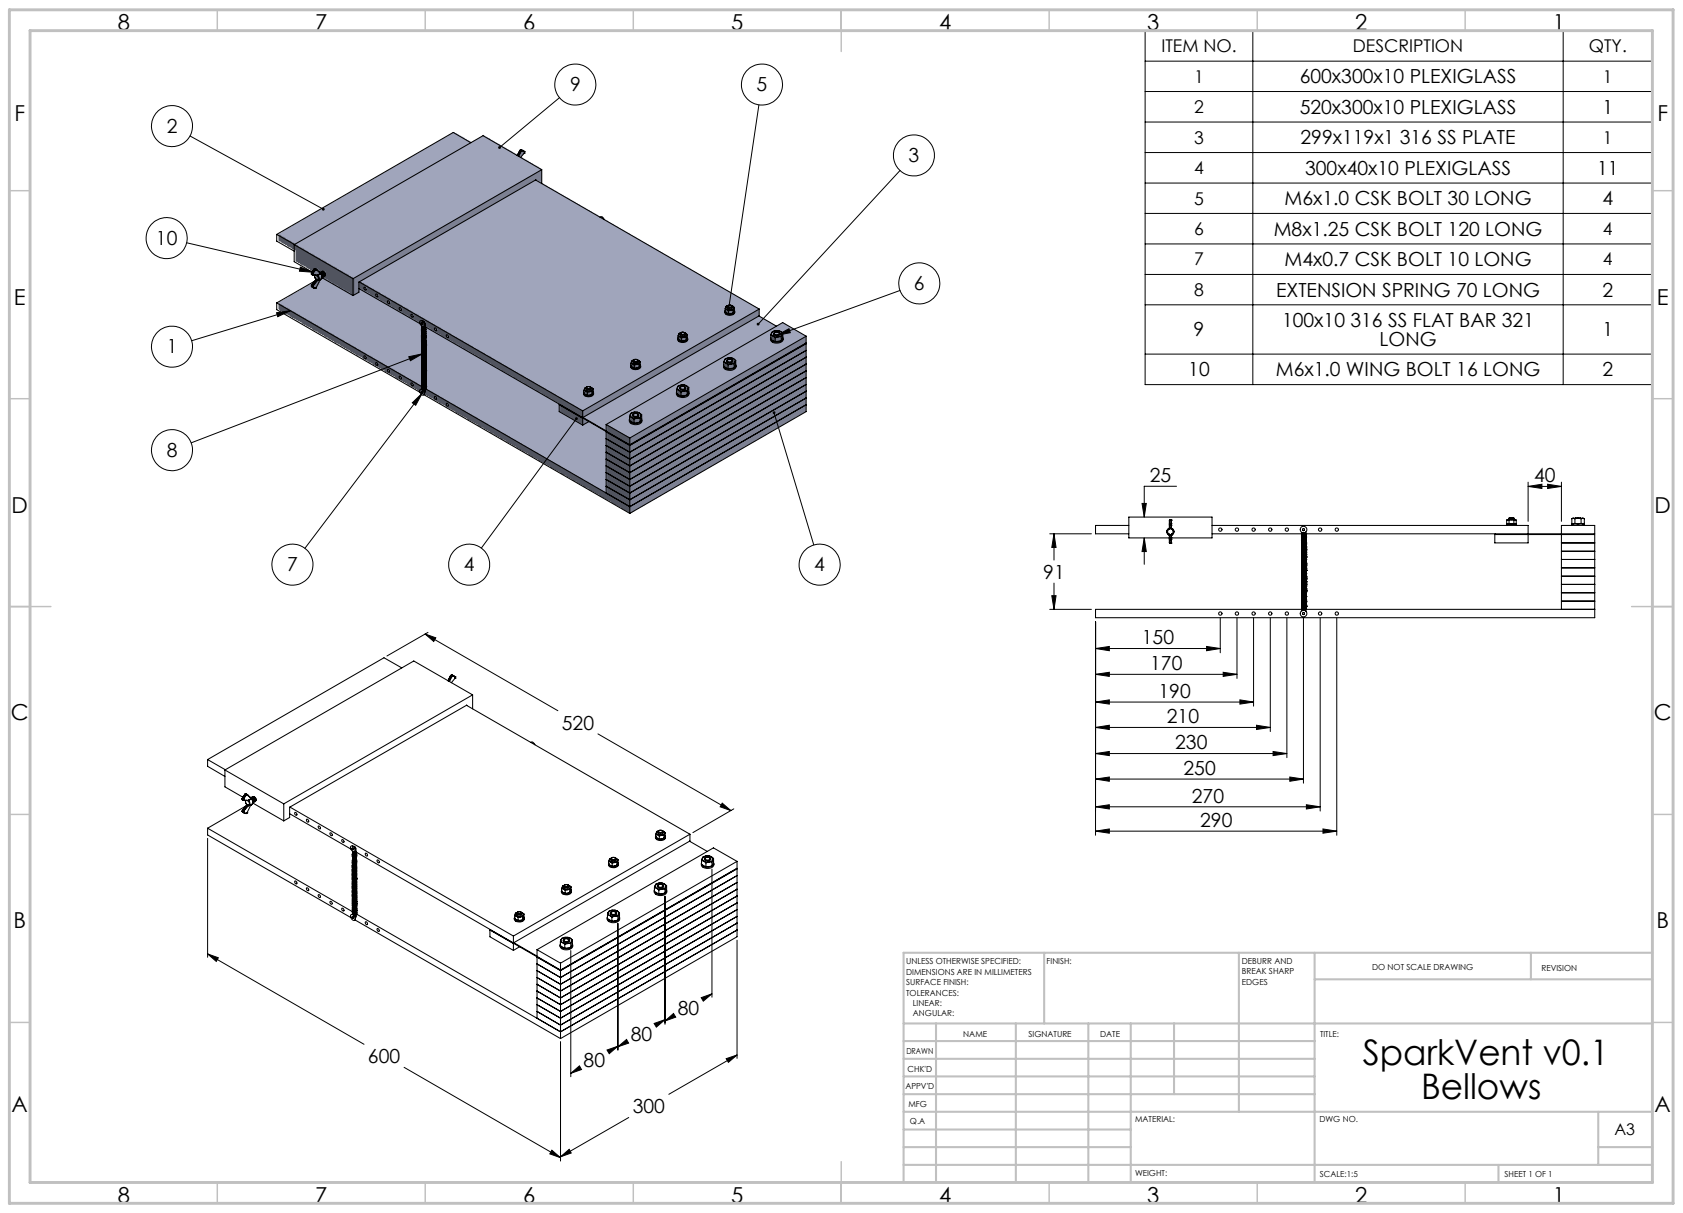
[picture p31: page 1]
FINISH:; DEBURR AND; BREAK SHARP; DO NOT SCALE DRAWING; REVISION; SCALE:1:5; SHEET 1 OF 1; Bellows A

ITEM NO. | DESCRIPTION | QTY.
1 | 600x300x10 PLEXIGLASS | 1
2 | 520x300x10 PLEXIGLASS | 1
3 | 299x119x1 316 SS PLATE | 1
4 | 300x40x10 PLEXIGLASS | 11
5 | M6x1.0 CSK BOLT 30 LONG | 4
6 | M8x1.25 CSK BOLT 120 LONG | 4
7 | M4x0.7 CSK BOLT 10 LONG | 4
8 | EXTENSION SPRING 70 LONG | 2
9 | 100x10 316 SS FLAT BAR 321 LONG | 1
10 | M6x1.0 WING BOLT 16 LONG | 2

UNLESS OTHERWISE SPECIFIED:
DIMENSIONS ARE IN MILLIMETERS
SURFACE FINISH:
TOLERANCES:
LINEAR:
ANGULAR:

NAME | SIGNATURE | DATE | | | | TITLE: SparkVent v0.1

DRAWN
CHK'D
APPV'D
MFG
Q.A | | | | MATERIAL: | DWG NO. | A3

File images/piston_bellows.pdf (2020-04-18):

## Oxygen Air

## Scavenger

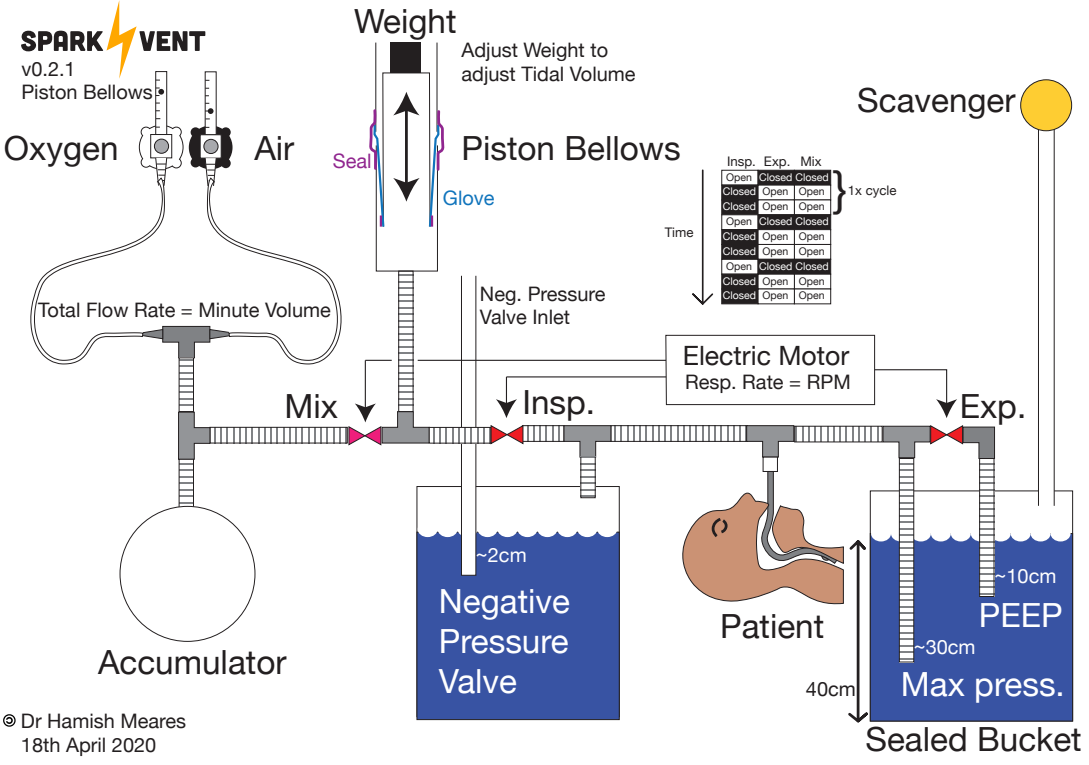
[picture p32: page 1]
Mix; Insp.; Exp.; PEEP Max press.; Patient; v0.2.1 Piston Bellows; 1x cycle }; Accumulator; Negative Pressure Valve; Weight; Total Flow Rate = Minute Volume; Neg. Pressure; Valve Inlet; Glove; Seal

Adjust Weight to
adjust Tidal Volume
Piston Bellows

Insp. Exp. Mix
Open Closed Closed
Closed Open Open
Time

Electric Motor
Resp. Rate = RPM

Sealed Bucket Dr Hamish Meares
18th April 2020

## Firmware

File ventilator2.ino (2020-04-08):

//Spark Vent relay operation using Arduino
//Cycles relay(s) off for double the time they are on
//On time is adjustable with potentiometer
//
// Jeremy Funke March 2020

//time in milliseconds
#define INHALE_MIN 400
#define INHALE_MAX 4000

//The relay connections
#define VALVE_PIN 7
#define VALVE_PIN2 2

//The potentiometer wiper
#define POT_PIN A0

#define LED_PIN 13

// the setup function runs once when you press reset or power the board
void setup() {
  Serial.begin(9600);
  // initialize pins
  pinMode(VALVE_PIN, OUTPUT);
  pinMode(LED_PIN, OUTPUT);
  
}

// the loop function runs over and over again forever
void loop() {
  float sensor = analogRead(POT_PIN); //read voltage of potentiometer

  //scale reading to minmax
  int inhale = ((INHALE_MAX - INHALE_MIN) * (sensor / 1024.0)) + INHALE_MIN;
  
  Serial.print(sensor);
  Serial.print(" knob = inhale for "); 
  Serial.print(inhale);
  Serial.println(" ms"); //print findings to serial console to check potentiometer is working as expected
  
  digitalWrite(LED_PIN, HIGH); // turn the relay on
  digitalWrite(VALVE_PIN, HIGH);
  digitalWrite(VALVE_PIN2, LOW);    
  delay(inhale);            // wait for a second
  digitalWrite(LED_PIN, LOW);    // turn the  relay off
  digitalWrite(VALVE_PIN, LOW);
  digitalWrite(VALVE_PIN2, HIGH);
  delay(inhale*2);                       // wait for a 2 seconds
}

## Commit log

2020-04-03 Add files via upload
    Arduino code to run relay(s).
2020-04-08 Added to Prototypes text
2020-04-11 Added 3D print files and instructions
    [Base.STL, Bearing Cap.STL, Bottom Pinch 3.3mm Gap.STL, Bottom Pinch 3.5mm Gap.STL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]
2020-04-18 Added hinged bellows and bucket diagrams
2020-04-20 Expiratory valve failure design flaw noted
2020-05-21 Adding Campbell SparkVent3
    [Adapter#1 Solid.STL, Adapter#1.STL, Adapter#3 Solid.STL, Adapter#3.STL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]
2020-05-21 Removing old parts list
    [Ventilator.xlsx]
